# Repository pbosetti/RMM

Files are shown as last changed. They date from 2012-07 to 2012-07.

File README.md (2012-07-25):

Software for Roundness Measuring Machine
========================================

This project hosts the code under development for the controller for a Roundness Measuring Machine developed at Stanford PRL.

**To download:** use git or get the zipball [here](https://github.com/pbosetti/RMM/zipball/master)

Content
=======
The `counter` folder contains the [Arduino](http://arduino.cc) firmware developed for controlling the spindle AC motor and for reading the rotary encoder [HEDS-9140](http://www.avagotech.com/docs/AV02-1132EN).

The `LabVIEW` folder contains the LabVIEW project that reads data from the Arduino and from the linear displacement gauge.

The `docs` folder contains the documentation. In particular, the `counter.fzz` file is a sketch representing the breadboard wiring for the Arduino board, prepared and readable with [Fritzing](http://fritzing.org).

Arduino firmware
================
The Arduino firmware (`counter/counter.ino`) is designed to be connected to the HEDS-9140 rotary encoder with a 5 poles cable. The [spec sheet](http://www.avagotech.com/docs/AV02-1132EN) reports the meaning of the 5 wires.

The firmware holds a global counter that counts the pulses and resets the count to zero at every turn. The artwork used with the counter can have different resolutions (ie number of pulses). Before compiling and uploading the firmware it **must be checked** that the preproc directive `STEPS` corresponds to the actual number of pulses **minus one** (the counter runs on 0-base).

Communication
-------------
The firmware can communicate with the USB host via serial communication at 115200 baud. The communication is ASCII-based and follows the same syntax:

- `i`: print out a device ID string
- `nnd`: set the loop delay to `nn` milliseconds (in range 1--1000)
- `/`: toggle between polling and continuous data flow. When in continuous mode, it routinely prints the current readings (the rate is set with the `nnd` command above, default to 10 ms)
- `p`: return the number of pulses of the configured artwork
- `p`: when in polling mode, return the current counter status string
- `M`: turn te relay controlling the AC motor on
- `m`: turn te relay controlling the AC motor off

In both polling and continuous mode, the status string has four space-separated fields that have the following meanings:

1. the first field is either 0 (homing *not* done yet) or 1 (homing done); it goes from 0 to 1 after the first incomplete turn, so the angular position is only reliable when this field is 1
2. reset. This field cycles from 0 to 1 every turn (0 the first run, 1 the second, 0 the third and so on). When it changes, a new turn is just begun
3. the actual counter, ranging from 0 to STEPS
4. the curent rotational velocity **CODE NOT RELIABLE YET!**

This simple protocol is used in the LabVIEW code for controlling the motor and readin the angular position.

Hardware
--------
The firmware is designed to have a small set of digital I/O providing user feedback and auxiliary functions.

- **Digital pin 5**: it is supposed to drive on/off the relay that controls the AC motor. The Fritzing sketch also shows an LED in parallel to the motor relay
- **Digital pin 6**: this pin provides user feedback about the HEDS-9140 encoder: when an LED is connected to this pin, it will toggle on and off at every pulse and--when on--its brightness will range from 0 to max as the counter goes from 0 to STEPS
- **Digital pin 7**: this pin is supposed to be connected to a pushbutton as shown in the sketch. Temporarily bringing this pin to HIGH (ie pushing the button) will toggle the motor on and off. *If not used, this pin MUST be grounded*
- **Digital pin 13**: this pin should be connected to a red LED, which will stay on until the first turn would be completed (ie homing performed).

*Note*: all LED must be protected from overcurrent with a 220 Ohm resistor in series.

<a href="https://github.com/downloads/pbosetti/RMM/counter_bb.png" target=blank>Arduino-based breadboard</a>

Author
======
Paolo Bosetti

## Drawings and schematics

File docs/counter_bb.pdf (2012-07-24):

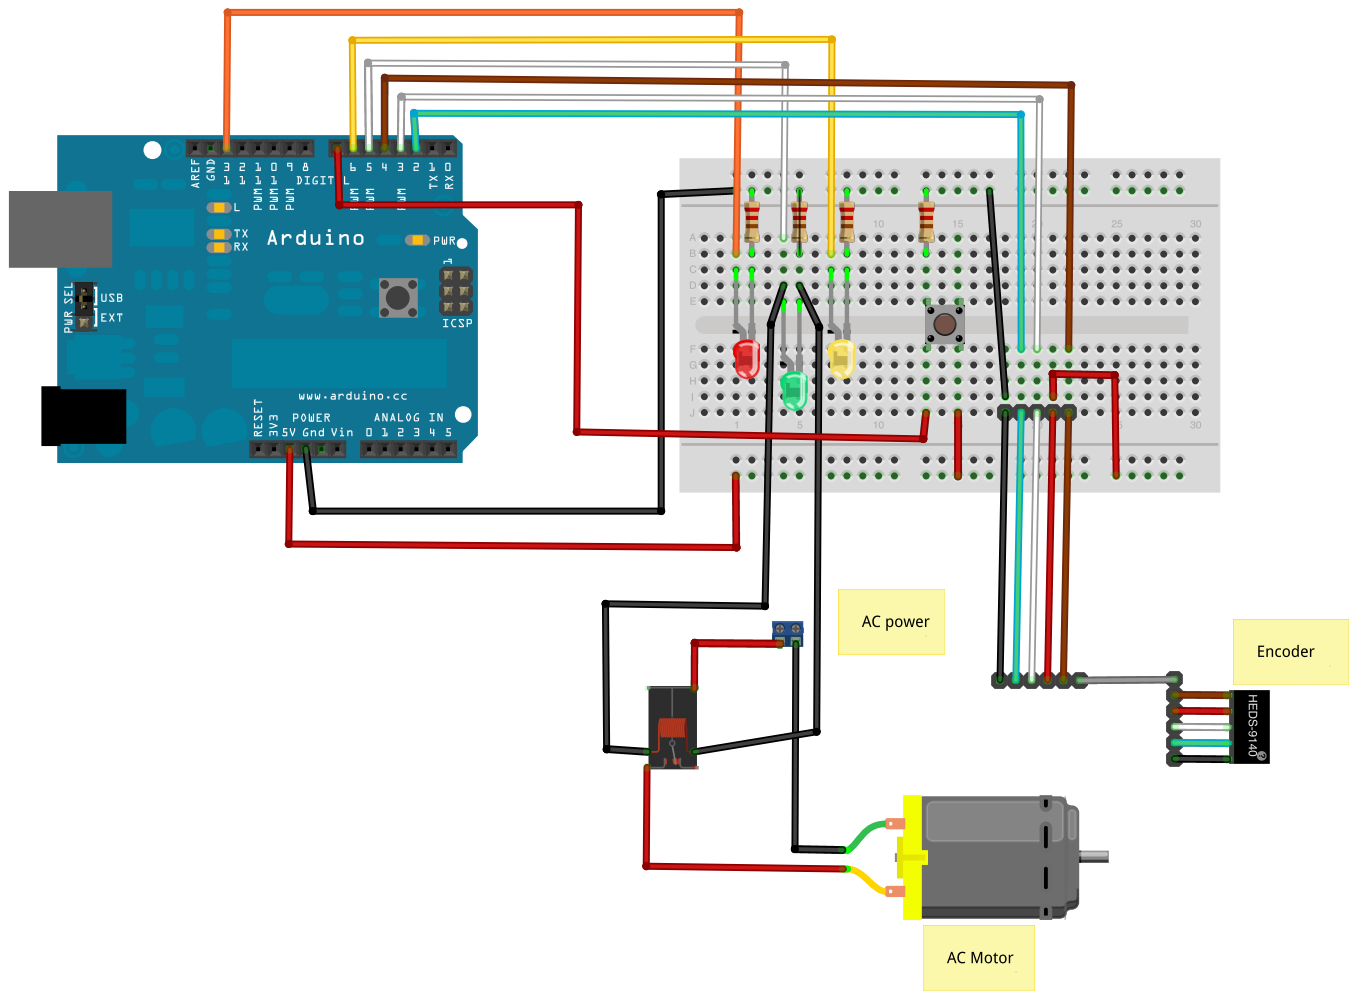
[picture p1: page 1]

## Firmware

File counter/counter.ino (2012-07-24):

/* Rotary encoder driver for HEDS-9150 quadrature encoder */
/* By Paolo Bosetti 2012 - paolo.bosetti@ing.unitn.it     */
/* Developed on the Arduino 1.0.1 IDE                     */

/* Defines. Change these values for configuring the system */
#define CODE_ID "RMM_counter 0.3"
#define BAUD  115200 // Serial communication baud rate
#define DELAY     10 // Main loop delay
#define STEPS    499 // Maximum step count on the artwork (base ZERO!!!)
#define CH_I       2 // Pin for index input (one per revolution)
#define CH_A       3 // pin fr Ch.A readout
#define CH_B       4 // Pin for Ch.B readout
#define RELAY      5 // Output pin for controlling the relais that drives the motor on or off
#define PLED       6 // Proportional LED
#define MOTOR_CTRL 7 // Connected to button that cycles motor on/off
#define LED       13 // Homing LED: Will stay on until the first reference has gone

/* GLOBALS */
float g_timescale = 1000000.0 / (float)(STEPS + 1) * 360;
/* Do not edit anything below this line!!! */
int g_counter;
unsigned int g_delay = DELAY;
bool g_home = HIGH;
bool g_reset = false;

/* ISR triggered by Ch.A */
void 
step()
{
  if (digitalRead(CH_B) == HIGH)
    g_counter--;
  else
    g_counter++;
  
  if (g_counter < 0)
    g_counter = STEPS;
  if (g_counter > STEPS)
    g_counter = 0;
  analogWrite(PLED, g_counter % 2 == 1 ? ((float)g_counter/(STEPS+1))*256 : 0);
}

/* ISR triggered by Ch.I */
void 
zero()
{
  g_counter = STEPS;
  g_home = LOW;
  g_reset = !g_reset;
  digitalWrite(LED, g_home);
}

void
print_status()
{
  unsigned long now = micros();
  static int last_counter = 0;
  static unsigned long last_time = micros();
  float v = g_timescale * (g_counter - last_counter) / (now - last_time);
    Serial.print(g_home == LOW ? 1 : 0);
    Serial.print(" ");
    Serial.print(g_reset ? 1 : 0);
    Serial.print(" ");
    Serial.print(g_counter);
    Serial.print(" ");
    Serial.println(v);
  last_counter = g_counter;
  last_time = now;
}

void 
setup()
{
  Serial.begin(115200);
  
  pinMode(CH_I,  INPUT_PULLUP);
  pinMode(CH_A,  INPUT_PULLUP);
  pinMode(CH_B,  INPUT_PULLUP);
  pinMode(RELAY, OUTPUT);
  pinMode(LED,   OUTPUT);
  pinMode(PLED,  OUTPUT);
  pinMode(MOTOR_CTRL, INPUT);
  
  digitalWrite(LED, g_home);
  digitalWrite(RELAY, LOW);

  attachInterrupt(0, zero, RISING);
  attachInterrupt(1, step, RISING);
}

void 
loop()
{
//  static int last_counter = 0;
  static bool polling = true;
  static bool motor = false;
  static unsigned long last_time = millis();
//  unsigned long now = micros();
  
  char ch;
  static unsigned long accumulator = 0;
  
  if (Serial.available()) {
    ch = Serial.read();
    switch(ch) {
    case '0'...'9':
      accumulator = accumulator * 10 + ch - '0';
      break;
    case 'i':
      Serial.println(CODE_ID);
      break;
    case 'd':
      g_delay = constrain(accumulator, 0, 1000);
      accumulator = 0;
      break;
    case '/':
      polling = !polling;
      break;
    case 'p':
      Serial.println(STEPS + 1);
      break;
    case '?':
      print_status();
      break;
    case 'M':
      motor = true;
//      digitalWrite(RELAY, HIGH);
      break; 
    case 'm':
      motor = false;
//      digitalWrite(RELAY, LOW);
      break;
    }
  }
  
  if (!g_home && !polling) {
    print_status();
  }
  
  static bool latch = false;
  if (digitalRead(MOTOR_CTRL) == HIGH and millis() > last_time + 500 and not latch ) {
    motor = ! motor;
    last_time = millis();
    latch = true;
  }
  if (digitalRead(MOTOR_CTRL) == LOW and latch)
    latch = false;
  digitalWrite(RELAY, motor ? HIGH : LOW);
  
  delay(g_delay);
}
